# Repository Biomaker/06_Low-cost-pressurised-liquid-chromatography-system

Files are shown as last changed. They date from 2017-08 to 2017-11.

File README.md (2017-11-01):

## Open-source pressurised liquid chromatography system for the purification of proteins and small molecules

## Synopsis

Column chromatography is a routine technique for the separation of components from complex mixtures. In biochemistry and molecular biology, the most common application is the purification of recombinantly expressed proteins from in vitro or in vivo expression systems. These separations are currently performed by gravity flow, centrifugation or by using automated systems that use pumps to force solutions over a column. 

Gravity flow and centrifugation techniques, while simple and relatively inexpensive, are labour intensive and time consuming. Conversely, commercial systems allow a high degree of automation, limiting hands-on time, and allow more complex elution protocols, such as elution using salt or pH gradients. However, these systems require specialised, expensive equipment. The project proposed here aims to produce a lower cost, modular, open-source alternative to these commercial systems for performing simple, routine purifications.

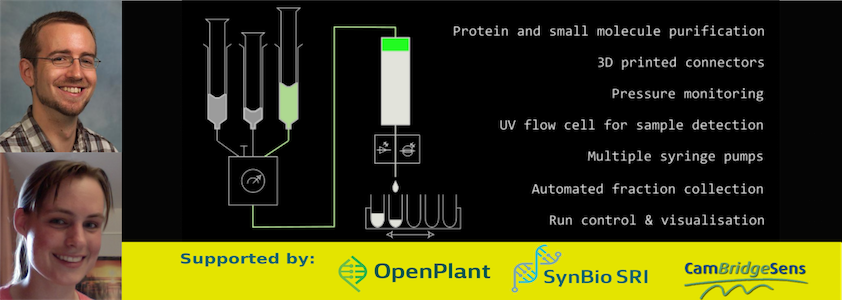
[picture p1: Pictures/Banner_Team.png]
Banner_image


## Overview Diagram

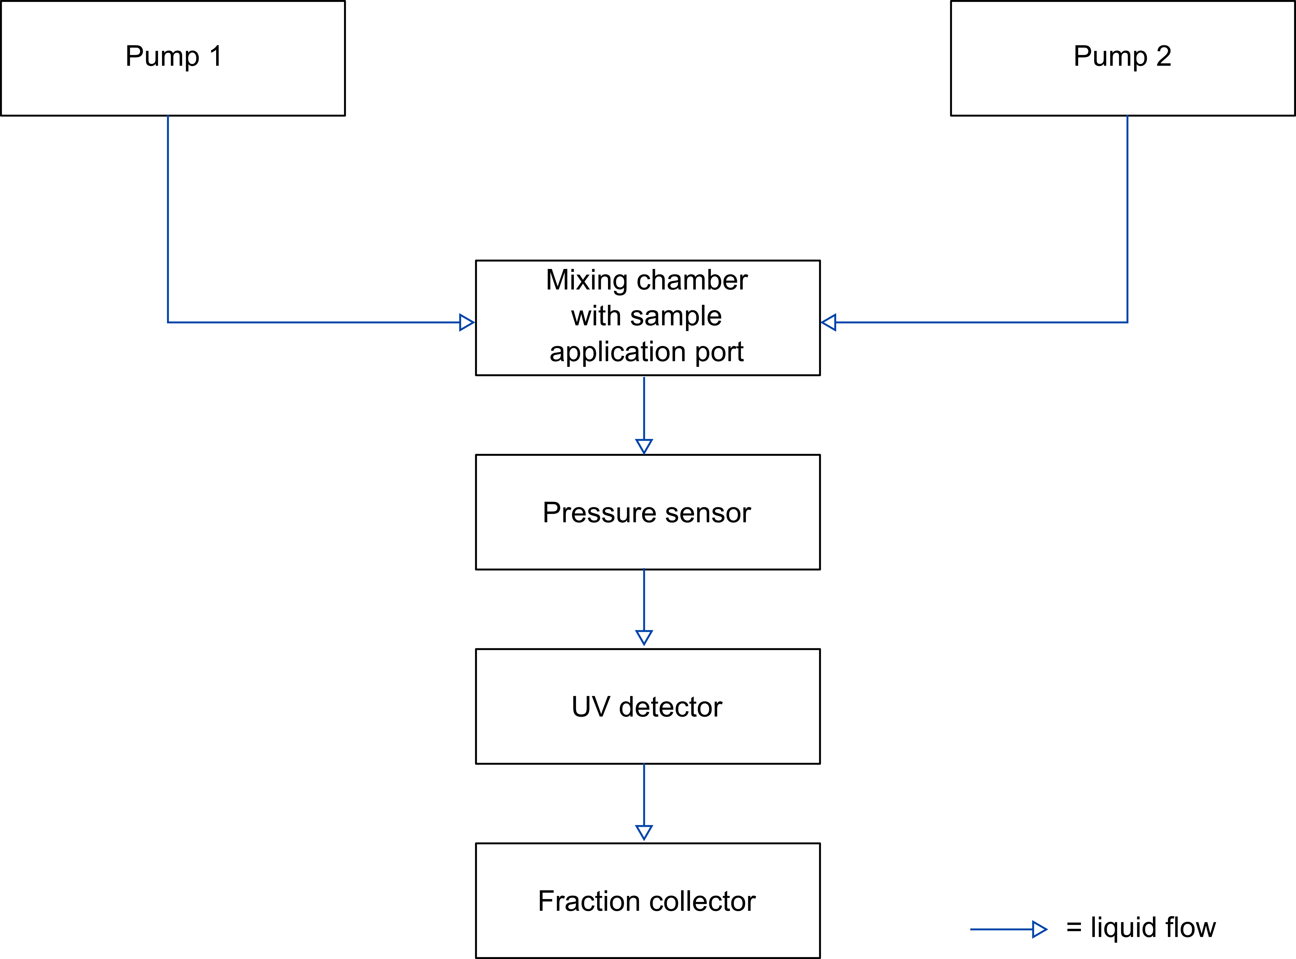
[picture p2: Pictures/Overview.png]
Project_overview


Diagram showing a high-level overview of the system. A typical method run for purification of a protein (preprogrammed in method runs) is as follows:
1) Connection of a chromatography column appropriate for the purification between the pressure sensor and UV sensor
2) Equilibration (conditioning) of the column using equilbration/wash buffer from pump 1
3) Loading of the sample through the sample application port on the mixing chamber
4) Washing of unbound material using equilbration/wash buffer from pump 1
5) Elution of the protein of interest from the column using elution buffer from pump 2
6) Steps 4 and 5 are accompanied by fractionation (separation of components) into different wells of a 96-well plate using the fraction collector

This project is a work in progress. For each component, navigate to the component folder for a list of known bugs and planned future improvements.

## Software
The project contains four Arduinos, one in each of two pumps, one in the fraction collector (SCARA arm) and one in the control unit. The control unit coordinates the other Arduinos and also reads out pressure sensor and UV sensor data. The SCARA arm Arduino controls the movements of the arm on prompting from the control unit over I2C. Pump Arduinos control the movement of the pumps after prompting by the control unit over I2C. For details of the software for each component, see the individual component folders.

## Hardware

The project contains different hardware modules, which are coordinated by the control module. For CAD files and diagrams, see individual component folders.

## Installation, Maintenance and Testing Guide

See individual component folders.

## Licenses

Hardware is distributed under the Creative Commons share alike license (see Thingiverse links). 
All software is available under the GNU General Public License Version 3 (https://www.gnu.org/licenses/gpl.html).

This project makes use of the following non-standard Arduino libraries, which are distributed under the indicated licenses:
1) Grove_LCD_RGB_backlight library - The MIT License (MIT) - Copyright (c) 2013 Seeed Technology Inc
2) MS5803-14 Master library for MS5803 14bar pressure sensor module - by Luke Miller (http://github.com/millerlp) -GNU General Public License Version 3

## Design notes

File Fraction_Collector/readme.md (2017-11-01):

 ## Fraction collector/SCARA Arm
 
 ## What does it do?
 A range of methods in a molecular biology laboratory is based splitting a sample in several sub-samples, commonly referred to as fractions. Depending on the method, fractions sometimes represent a spatial separation (e.g. when transferring liquids of ‘slices’ of a centrifugation tube into separate fractions), or temporal (e.g. when fraction are created from liquids running over a chromatography column). The common factor is that a certain amount of liquid is dispensed into a reservoir, then another one, then another one, and so on. Each of these fractions can then be treated independently  - to measure concentrations of compounds, enzymatic activities or just check what they smell like.
 
A fraction collector is fundamentally a piece of equipment that can hold a number of containers, and moves them about when required. 
 
 ## How is it implemented?
 
 Basic requirements:
-	use a flexible robotic arm with a small foot print when not in use
-	exchangeable tool head to accommodate a range of reservoirs

    o	SBS 96-well plate (shallow/deep)
    
    o	Eppendorf tubes
    
    o	Other reservoirs
    
-	Use common hardware from the 3D printing community
-	Focus on 3D printed parts to minimize commercial parts
-	Make something more exciting than a standard 2-axis plotter

We decided to use a 2D SCARA design (Selective Compliance Articulated Robot Arm) that was designed from scratch with an eye on minimizing exotic hardware. It is powered by NEMA 17 servos and Arduino hardware, using driver boards from the RepRap 3D printing community and cheap GT2 belts with 3D printed belt clamps. In order to save cost, we avoided optical or other encoders, and solely rely on an initial calibration step using microswitches to determine the absolute position of the arm. 

A carrier plate at the ‘wrist’ of the arm can hold a number of reservoirs, with the primary design focusing on standardized 96 well plates in an SBS format.  Other holders can be easily designed and programmed for.

The open source design should allow easy integration and adoption of this fraction collector for purposes other than chromatography
 
 ## Description of files
 Will be added when finished.
 
 ## Future work/Known bugs
 Future work:
 - add support for Eppendorff tubes and other reservoirs, other than the 96-well plate added so far
 
 Known bugs:
 - fraction collection is not accurate due to the code not taking into account the angle of the arm when aiming for the wells. Work is in progress on fixing the code

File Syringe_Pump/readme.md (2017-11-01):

## Syringe pumps

## What does it do?
A liquid chromatography setup relies on the controlled flow of liquid over a chromatography column. To provide this flow, we implement two syringe pumps, which can be programmed to flow at a desired flow rate. The system has two pumps, connected via a mixing chamber to potentially allow the use of a mixture of two buffers at ratios defined by the respective flow rates.

## How is it implemented?

## Description of files
Syringe_Pump_3_0_pump1 and Syringe_Pump_3_0_pump2 -> Arduino sketches, each controlling one pump. The only difference between the two sketches is the I2C address, which allows the pumps to be controlled from the control unit.

3D printer files -> contains CAD and 3D printer files for the syringe pump hardware

## Future work/Known bugs

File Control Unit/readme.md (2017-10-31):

## Control unit

## What does it do?
The control unit coordinates the function of the other components of the FPLC. It checks if all devices are connected and provides feedback. It then sends a signal to the fraction collector to start its calibration. Users can then choose from a number of options to run the FPLC system either manually, or make use of pre-programmed methods.

To save on Arduinos and reduce communication, the control unit also reads out the values from the pressure and UV sensors in our implementation. 

## How is it implemented?
The control unit communicates with the other devices over I2C. For display, it uses the Seeed kit Grove RGB LCD. To navigate the menus, it makes use of five buttons, connected via different resistors to one analog pin on the Arduino. Depending on the analog value received, the Arduino can determine which button has been pressed.

The menu layout is as follows:
1) Start/Welcome screen
2) Check I2C communication to all connected devices and display if devices are connected - allow user to repeat the test if desired
3) Start fraction collector calibration
4) Allow choice between Manual Run or Method Run:

5) Manual Run - Select either which pump to run at which speed -> this will trigger the selected pump and tell it to run at the speed specified via I2C, or select Display sensor values. Display sensor values will display current values from the pressure sensor (in bar) and the UV sensor

6) Method Run - Currently the unit has two pre-programmed methods- a pump wash method, which will first run pump 2 and then pump 1 to wash out residual buffer from a previous run and prefill the tubing with the solution from pump 1. The second method is a standard run method, which first runs pump 1, pauses to allow loading of the sample, runs pump 1 while collecting fractions and then runs pump 2 while collecting fractions. During the entire program, UV and pressure sensor readings are displayed. The current program assumes a 1 ml column.

For implementation of the UV sensor and pressure sensor, see the respective subfolders.

## Description of files
Control_unit_1_4                      -> latest Arduino sketch for running the control unit

MCU v3.step                           -> CAD file for control unit enclosure

MCU_base.stl and MCU_cover.stl        -> 3D printer files for enclosure

Fritzing Files                        -> Diagrams for the pressure sensor and a Fritzing file for the circuit

MCU_BOM_electronics.md                -> Bill of materials for the electronics

MCU_Fritzing.pdf                      -> Picture of the Fritzing breadboard diagram buttons are (from left to right) - UP, DOWN, LEFT, RIGHT, SELECT

## Future work/Known bugs/issues

Future work:
- Bug fixing - see below
- Allow saving of the UV and pressure sensor information to an SD card
- Allow display of the UV and pressure sensor information as it relates to the fractions after the run
- Build a display and analysis program on a Raspberry Pi for display and processing of run data
- Allow user to add pre-programmed methods using the display and analysis program

Known bugs:
- UV sensor readings are not very sensitive and too low to be of use - could potentially be fixed by reducing the flow path distance and using a more powerful UV light source

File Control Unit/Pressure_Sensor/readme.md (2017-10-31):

## Pressure Sensor

## What does it do?
In a liquid chromatography system, the column represents a key component. Resins with specific properties tend to be expensive, and can be easily damaged by incorrect handling. 

The rate at which samples or liquids can be pushed through the column is not constant, and can be drastically reduced if a column is overloaded. If the flow rate is not reduced at this point, the column or other components can be damaged by the increasing back pressure.

## How is it implemented?
We decided to use the  MS5803-14BA sensor, as it can communicate by I2C and is protected against the liquid phase by a gel membrane cover. 

We bought a non-integrated sensor to minimize cost, but would advise against this course of action, as the SMD packaging format makes soldering difficult. We succeeded in soldering the sensor to an SMT breakoutPCB for SOIC-8 from Adafruit (Product nr. 1212), using a hot plate and a heat gun. For easier use, we would recommend the SparkFun Pressure Sensor Breakout Board MS5803-14BA (SEN-12909).

The sensor is integrated into the chromatography setup using a 3D printed part with a suitable cut-out for the sensor. The sensor and board were constrained by a clamp, and any gaps closed by silicone sealant. 

To allow reading of the sensor values using an Arduino, we made use of the MS5803-14 Master library by Luke Miller, which can be found at http://github.com/millerlp. His repository also contains sketches for testing the sensor, which we used to verify our sensor was working prior to integration into the control unit.

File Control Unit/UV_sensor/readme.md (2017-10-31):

## UV flow cell

## What does it do?
During a chromatography run the protein of interest is held back on the column until a specific buffer reaches the column and washes the protein off the column – this is referred to as elution. The fraction collector will create a sequential series of samples coming off the column, some of which will contain the protein.  How can we identify which fractions are valuable to us?

Most proteins in solution can not be seen by the naked eye in the visible light spectrum, but a majority absorbs UV light. By shining a constant amount of UV light through the sample and measuring how much UV light exits at the other side of the sample, we can identify fractions that contain the largest amount of protein and therefore absorb the largest amount of UV light This can either be done after the purification is finished, but most modern FPLC systems would constantly monitor these measurements while the sample is separated into fractions.

Proteins that contain amino acids with aromatic rings (Tryptophan, Tyrosine) absorb light at 280 nm (UV). In a photometer, light is filtered down to a specific wavelength or wavelength range, directed through the sample and the transmitted light detected. The resulting signal is dependent on the distance through the sample, the concentration of protein in the sample and the specific absorption coefficient. This relationship is described by the Beer-Lambert Law.

## How is it implemented?

Requirements:
-	small volume in the flow cell to minimize dead volume 
-	280 nm light must not be absorbed by the container
-	pressure proof
-	280 nm light must be contained to ensure safety
-	cheap

Commercial flow cells tend to cost hundreds of pounds. They rely on glass or quartz chambers which are UV permissive, and use strong, wide-band light sources to allow flexible measurements of various wavelengths, to allow flexible detection of various compounds depending on the application. 

We decided to create a cheap flow cell based on disposable plastic cuvettes that are transparent to UV light. They create a 10 mm path length through the sample, but are normally not suited to continuous usage. By designing a custom 3D printed plug, we created a small enclosed chamber around the light path, with two tubes allowing continuous flow into and out of the cuvette. 
Monochromators, which filter out unwanted wavelengths, are similarly complex and expensive. We therefore bought a 12V 280nm UV LED, with a  narrow emission spectrum, and combined it with a cheap wideband UV detector (280-390nm). While this would normally be not desirable, in a closed system the vast majority of the signal will be generated by the 280nm LED.

The 3D printed enclose creates a housing for the plastic cuvette, creates holders for both the LED and the UV detector and allows a tight connection with the plug. Generous use of silicone sealant both avoids leakage of liquids and light outside the desired light path.

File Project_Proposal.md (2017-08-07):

## Summary
Column chromatography is a routine technique for the separation of components from complex mixtures. In biochemistry and molecular biology, the most common application is the purification of recombinantly expressed proteins from in vitro or in vivo expression systems. These separations are currently performed by gravity flow, centrifugation or by using automated systems that use pumps to force solutions over a column. 
Gravity flow and centrifugation techniques, while simple and relatively inexpensive, are labour intensive and time consuming. Conversely, commercial systems allow a high degree of automation, limiting hands-on time, and allow more complex elution protocols, such as elution using salt or pH gradients. However, these systems require specialised, expensive equipment. The project proposed here aims to produce a lower cost, modular, open-source alternative to these commercial systems for performing simple, routine purifications.

## Proposal
Systems to be used and problems to be addressed
Research into protein structure and function relies heavily on the availability of highly pure proteins. These are routinely produced in recombinant expression systems and purified using a variety of chromatography methods, such as affinity purification, ion exchange or size exclusion chromatography.
 
There are a variety of methods available for applying samples and solutions to chromatography columns, each with their advantages and disadvantages. Gravity flow and spin column purification, while having the advantage of being relatively low-cost, are labour intensive, requiring manual sample and buffer addition and are also limited in terms of complexity of the elution conditions. Gravity flow and spin column purification are therefore mainly used for the purification of limited amounts of protein using various types of affinity purification. For large-scale purifications or purification requiring more complex elution conditions, such as salt or pH gradients, automated FPLC (fast protein liquid chromatography) systems are commonly used. These systems use pumps to force solutions over chromatography columns at pressure and thereby reduce run time. They also allow the use of preprogrammed complex purifications to take place without manual intervention. Their major drawback is their cost, with entry level models starting at roughly 5,000 GBP.
 
## Design goals and implementation 
We aim to create a system that sits in between the manual purification methods and the fully automated, specialised systems. The goals and proposed design steps for this system are as follows:

1)	Automate a gravity flow procedure with automated sample loading, washing and elution using a single elution buffer (step elution) for affinity purification. 
Initially, we will use three syringe pumps for wash solution, elution solution and sample solution respectively. These will be placed on a 3D-printed rack, to allow them to be moved with respect to the column. For the syringe-based pump system, we will adapt an existing open-source design, described here: (http://www.appropedia.org/Open-source_syringe_pump). We aim to allow for programming of the device via a simple UI on an embedded screen.

2)	Automated fraction collection
The fraction collector will take the form of a movable tube rack. The design will be based on a linear slider mechanism that will be either 3D printed or based on aluminium extrusions.

3)	Conversion of the gravity flow system to a pressurised closed system
We intend to use standard connectors (e.g. Luer) and silicone or Tygon tubing to connect the syringe pumps to the chromatography column. We will attempt to 3D print suitable connectors to maximize the usage of non-commercial parts. 

4)	On-line detection of protein using a custom-built detection module, display of results on fraction rack
To allow monitoring of the purification, we will add a detection module to the column outlet. This detection module will monitor protein concentration by absorbance at 280 nm in solution using a suitable UV LED and photodetector. Absorbance over time will be displayed on the embedded screen as well as on embedded LEDs in the fraction rack to indicate directly which tubes contain eluted protein.

More ambitious, additional goals, depending on success of initial designs would include:

1) Addition of valves/mixing chambers to the pump system to allow buffer mixing for running gradient elutions

2) Design of additional detection modules (e.g. DNA, absorbance at 260 nm) or fluorescence detection, which can be added to, or replace the 280 nm detector.

3) Addition of multiple pump and detector modules to allow parallel purification of multiple samples.

## Proposed outcomes and benefits
The major outcome of this project would be a low-cost, automated protein purification system, which could be used for simple, routine purifications in settings where gravity flow is too time consuming, but the cost of a commercial system is prohibitive. The open-source design will allow users to easily replace damaged parts as well as add to and customise the modules. Given the expected cost, we also see a use as a teaching tool for schools, undergraduate labs and biomaker spaces, to teach more advanced protein purification techniques and introduce students to the concept of automation in protein purification. The final 3D models, parts list, circuit diagrams, code and guides on replicating the project will be made available on Github for easy replication of the project.

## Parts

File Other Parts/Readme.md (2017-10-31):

This folder contains the 3D files for non-major devices. Including:
- the housing for the pressure sensor (required 2 knurled brass insert nuts & solid amount of glue)
- the swing arm to hold the tubing over the fraction collector (with mounting point for a laser module)
- the mixing unit to combine liquid from two pumps (requires more knurled brass insert nuts and two 3-way luer loc valves)

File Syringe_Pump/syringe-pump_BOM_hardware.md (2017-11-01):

Syringe Pump

Bill of materials 

-	Core 3D printed parts
-	1 x Stepper Motor NEMA-17 Size - 200 Steps/Rev, 12V 350mA
-	ProtoShield Protoyping Board for Arduino
-	1 x StepStick 4-layer DRV8825 Stepper Motor Driver boards
-	12V DC Connector 2.1x5.5mm DC Power Cable Jack Adapter
-	
-	3 x button microswitch
-	1 x 5 mm LED
-	2 x 30 cm 6mm steel rod 30 cm (depending on syringe)
-	1 x 30 cm M5 threaded rod 30 cm
-	1 x shaft coupler M5 
-	2 x LM6UU linear bearing 6 mm
-	1 x M5 knurled thumb nut, thin type (or other flat, wide M5 nut)
-	Various M3 screws for assembly 

Notes:

Top plate: print with 10-20% infill to create a sturdy structure. The linear bearings should fit snugly into the slots, 
same with the thumb screw (perhaps fix all with a dab of glue once the threaded rod holds it in place). 
The current version is designed for most 50/60ml syringes, but we have encountered syringes with unusual 
thickness/shape at the top of the plunger that wouldn’t fit – carving for a few minutes with a Stanley 
knive (on the syringe, not the 3D printed part) usually solved any problems.

Syringe adapter: The luer loc doesn’t fit perfectly yet, and will probably leak. 
Install a brass nut insert at the bottom (use a mixture of heat (soldering iron) and epoxy to fuse it tightly into the PLA), 
and then install the tubing with the printed connector screw, a rubber o-ring and any other sealing helpers (silicone, Teflon tape).  
Verify water tight fit, then install in the base unit. 

Base assembly: This is somewhat tight. A standard Arduino Uno just about fits into the base, and will support some of the pressure from the top. 
The vertical rods are supposed to be connected to two wires to carry power to the emergency off (maximum) button switch 
sitting on the holder. Conductive ink helps connector the wires in the 6mm rod slots to the rods themselves, otherwise soldering is an option. 
Similarly, the horizontal clamp has a slot for a short wire & a button switch to allow the pump to sense when it shouldn’t move any lower.
Install the two button switches & the LED at the front of the base.
Mount the Arduino against the vertical wall with two screws.
Fix the 12V connector in place with the clamp (and/or some glue). 
Place the finished prototyping board on top, then carefully close up the base. 

If it doesn't click into place, check for wires that got in the way.

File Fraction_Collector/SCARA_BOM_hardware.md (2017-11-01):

SCARA fraction collector

Bill of materials 

-	Core 3D printed parts: upper & lower arm, base, top 
-	Extra 3D printed parts: plate holder, switch housing, Arduino housing
-	https://www.thingiverse.com/thing:2613742
-	2 x Stepper Motor NEMA-17 Size - 200 Steps/Rev, 12V 350mA
-	2 x 2GT / GT2 timing belt sprocket, 20 teeth
-	1 meter 2GT / GT2 belt
-	3 x belt clamps (3D printed, https://www.thingiverse.com/thing:2503261)
-	Arduino Mega
-	ProtoShield Protoyping Board for Arduino
-	2 x StepStick 4-layer DRV8825 Stepper Motor Driver boards
-	4 x SPDT NO+NC KW12 Straight Hinge Lever Control Mini Micro Switch
-	6 x 625z ball bearings
-	12V DC Connector 2.1x5.5mm DC Power Cable Jack Adapter
-	M5 screws (e.g. M5 30-40mm connector bolt)
-	6 mm smooth steel rod, 10-30cm
-	2 x M5 binding screw 33mm (or normal M5 & nuts, for the elbow)
-	10 x M3 screws (3-5mm)
-	Silly amounts of wire
-	Some glue
-	Extra electronics (resistors, etc) see wiring diagrams. 

Notes: 
2GT / GT2 profiles for the arms are designed according to the official specification, 
with the sprocket on either arm sporting 90 teeth, matched to a 20 teeth sprocket on the stepper motor. 

Print parts and remove support structures as required.
Add 625z ball bearings into both arms and the roller unit, perhaps fix with a dab of glue (depending on the print quality).
Cut 2GT /GT2 belt to size, assemble around the arm and fix with the belt clamps. 
Adjust tension carefully – preferably when the arm is mounted to the base.
Adjust the relative positions of the belt clamps if they block each other during operations.
Glue microswitches into the housing (recommend rear-most slot on the side, lever facing up & lever facing down at the front).

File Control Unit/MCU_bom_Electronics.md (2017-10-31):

<!DOCTYPE html PUBLIC "-//W3C//DTD XHTML 1.0 Transitional//EN" "http://www.w3.org/TR/xhtml1/DTD/xhtml1-transitional.dtd">
<html xmlns="http://www.w3.org/1999/xhtml">
<body>
<h1>Bill of Materials: MCU.fzz</h1>
<p class="meta">MCU.fzz</p>
<p class="meta">Tuesday, October 31 2017, 23:30:00</p>

<h2>Assembly List</h2>
<table>

  <thead>
   <tr>
    <th>Label</th>
    <th>Part Type</th>
    <th>Properties</th>
    </tr>
  </thead>
  <tbody>
  <tr>
    <td>C1</td>
    <td>Ceramic Capacitor</td>
    <td class="props">voltage 6.3V; package 200 mil [THT, multilayer]; capacitance 100nF</td>
</tr><tr>
    <td>Grove1</td>
    <td>Grove RGB LCD 2 x 16</td>
    <td class="props">size 2 x 16; interface I2C; variant variant 13</td>
</tr><tr>
    <td>MS5803-14BA1</td>
    <td>MS5803-14BA Pressure Sensor</td>
    <td class="props">variant variant 1</td>
</tr><tr>
    <td>Part1</td>
    <td>Arduino Uno (Rev3) - ICSP</td>
    <td class="props">type Arduino UNO (Rev3) - ICSP (w/o icsp2)</td>
</tr><tr>
    <td>Part2</td>
    <td>Logic Level Converter</td>
    <td class="props"></td>
</tr><tr>
    <td>Part3</td>
    <td>GUVA-S12SD UV Light Sensor</td>
    <td class="props">variant variant 1</td>
</tr><tr>
    <td>R1</td>
    <td>220Ω Resistor</td>
    <td class="props">resistance 220Ω; package 0603 [SMD]; tolerance ±5%</td>
</tr><tr>
    <td>R2</td>
    <td>560Ω Resistor</td>
    <td class="props">resistance 560Ω; package 2512 [SMD]; tolerance ±5%</td>
</tr><tr>
    <td>R3</td>
    <td>1.7kΩ Resistor</td>
    <td class="props">resistance 1.7kΩ; package 2512 [SMD]; tolerance ±5%</td>
</tr><tr>
    <td>R4</td>
    <td>4.7kΩ Resistor</td>
    <td class="props">resistance 4.7kΩ; package 2512 [SMD]; tolerance ±5%</td>
</tr><tr>
    <td>R5</td>
    <td>10kΩ Resistor</td>
    <td class="props">resistance 10kΩ; package 2512 [SMD]; tolerance ±5%</td>
</tr><tr>
    <td>R6</td>
    <td>10kΩ Resistor</td>
    <td class="props">resistance 10kΩ; package 2512 [SMD]; tolerance ±5%</td>
</tr><tr>
    <td>R7</td>
    <td>10kΩ Resistor</td>
    <td class="props">resistance 10kΩ; package 0603 [SMD]; tolerance ±5%</td>
</tr><tr>
    <td>R8</td>
    <td>10kΩ Resistor</td>
    <td class="props">resistance 10kΩ; package 0603 [SMD]; tolerance ±5%</td>
</tr><tr>
    <td>S1</td>
    <td>Pushbutton</td>
    <td class="props">package [THT]</td>
</tr><tr>
    <td>S2</td>
    <td>Pushbutton</td>
    <td class="props">package [THT]</td>
</tr><tr>
    <td>S3</td>
    <td>Pushbutton</td>
    <td class="props">package [THT]</td>
</tr><tr>
    <td>S4</td>
    <td>Pushbutton</td>
    <td class="props">package [THT]</td>
</tr><tr>
    <td>S5</td>
    <td>Pushbutton</td>
    <td class="props">package [THT]</td>
</tr>
  </tbody>
</table>
<h2>Shopping List</h2>
<table>
  <thead>
	<tr>
    <th>Amount</th>
    <th>Part Type</th>
    <th>Properties</th>
    </tr>
  </thead>
  <tbody>
<tr>
    <td>1</td>
    <td>Ceramic Capacitor</td>
    <td class="props">voltage 6.3V; package 200 mil [THT, multilayer]; capacitance 100nF</td>
</tr><tr>
    <td>1</td>
    <td>Grove RGB LCD 2 x 16</td>
    <td class="props">size 2 x 16; interface I2C; variant variant 13</td>
</tr><tr>
    <td>1</td>
    <td>MS5803-14BA Pressure Sensor</td>
    <td class="props">variant variant 1</td>
</tr><tr>
    <td>1</td>
    <td>Arduino Uno (Rev3) - ICSP</td>
    <td class="props">type Arduino UNO (Rev3) - ICSP (w/o icsp2)</td>
</tr><tr>
    <td>1</td>
    <td>Logic Level Converter</td>
    <td class="props"></td>
</tr><tr>
    <td>1</td>
    <td>GUVA-S12SD UV Light Sensor</td>
    <td class="props">variant variant 1</td>
</tr><tr>
    <td>1</td>
    <td>220Ω Resistor</td>
    <td class="props">resistance 220Ω; package 0603 [SMD]; tolerance ±5%</td>
</tr><tr>
    <td>1</td>
    <td>560Ω Resistor</td>
    <td class="props">resistance 560Ω; package 2512 [SMD]; tolerance ±5%</td>
</tr><tr>
    <td>1</td>
    <td>1.7kΩ Resistor</td>
    <td class="props">resistance 1.7kΩ; package 2512 [SMD]; tolerance ±5%</td>
</tr><tr>
    <td>1</td>
    <td>4.7kΩ Resistor</td>
    <td class="props">resistance 4.7kΩ; package 2512 [SMD]; tolerance ±5%</td>
</tr><tr>
    <td>2</td>
    <td>10kΩ Resistor</td>
    <td class="props">resistance 10kΩ; package 2512 [SMD]; tolerance ±5%</td>
</tr><tr>
    <td>2</td>
    <td>10kΩ Resistor</td>
    <td class="props">resistance 10kΩ; package 0603 [SMD]; tolerance ±5%</td>
</tr><tr>
    <td>5</td>
    <td>Pushbutton</td>
    <td class="props">package [THT]</td>
</tr>
  </tbody>
</table>
<p class="meta"><br/>Exported with Fritzing 0.9.3- http://fritzing.org</p>
</body>
</html>

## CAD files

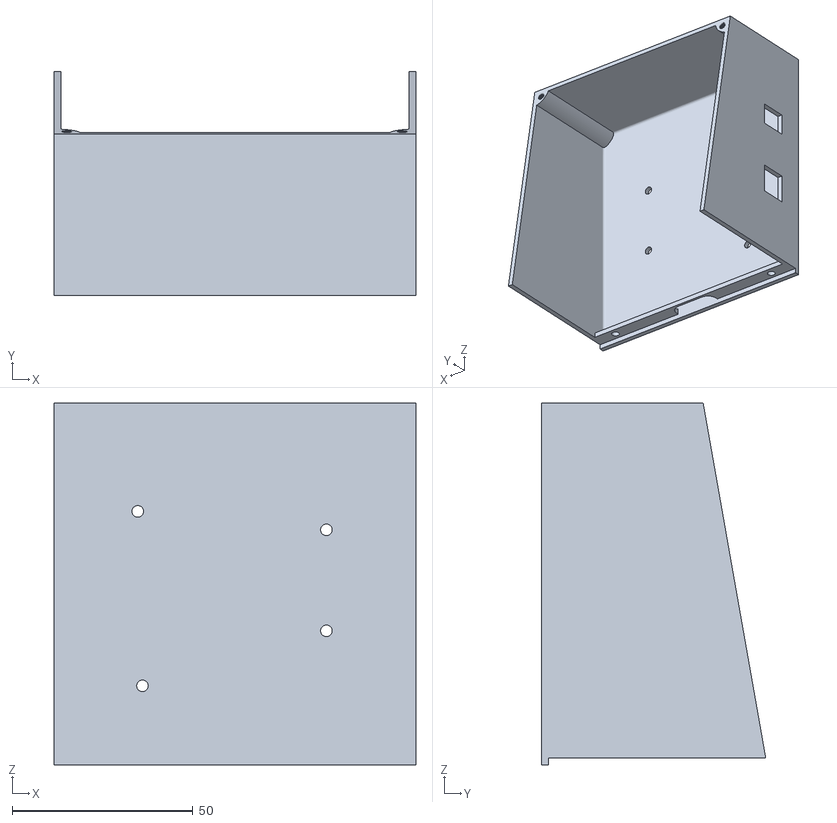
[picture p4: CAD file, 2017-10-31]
Control Unit/MCU_base.stl
100.0 x 62.0 x 100.0

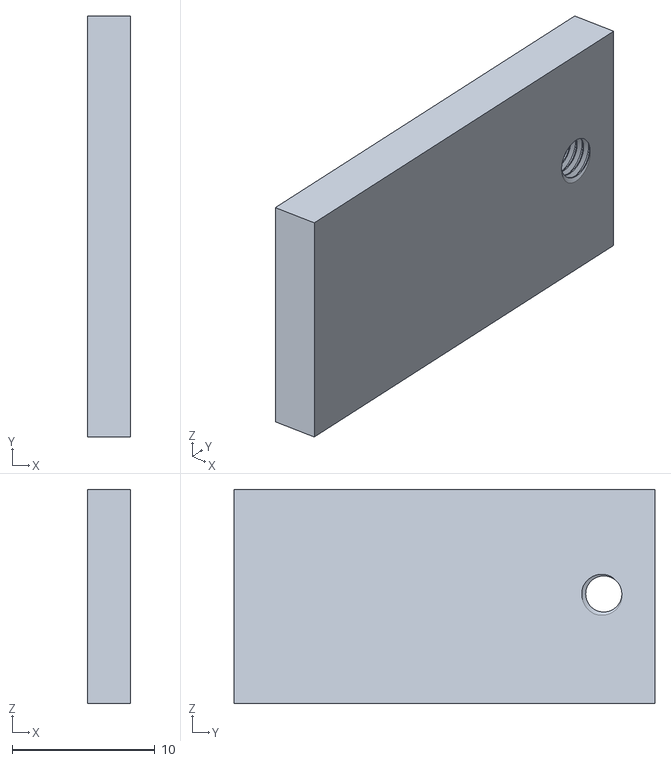
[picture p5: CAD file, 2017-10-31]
Control Unit/UV_sensor/flowcell_cover_led.stl
3.00 x 29.5 x 15.0

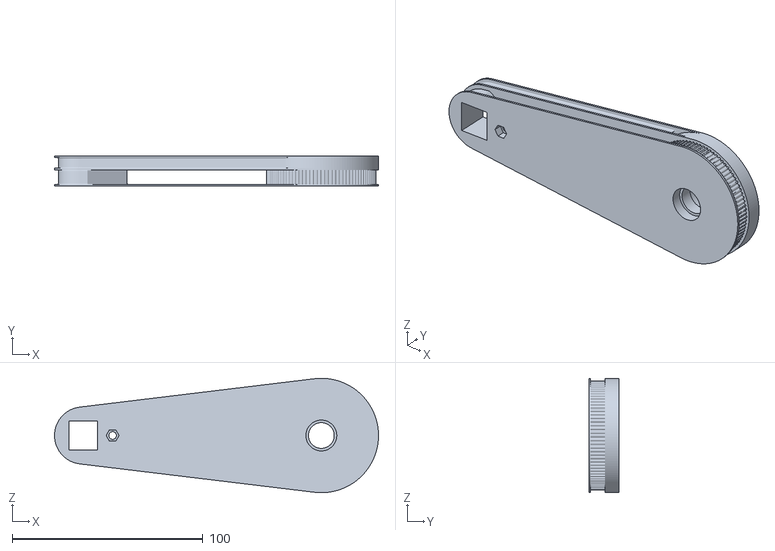
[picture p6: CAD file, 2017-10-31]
Fraction_Collector/3D printer files/scara_lowerarm.stl
170.0 x 16.0 x 60.0

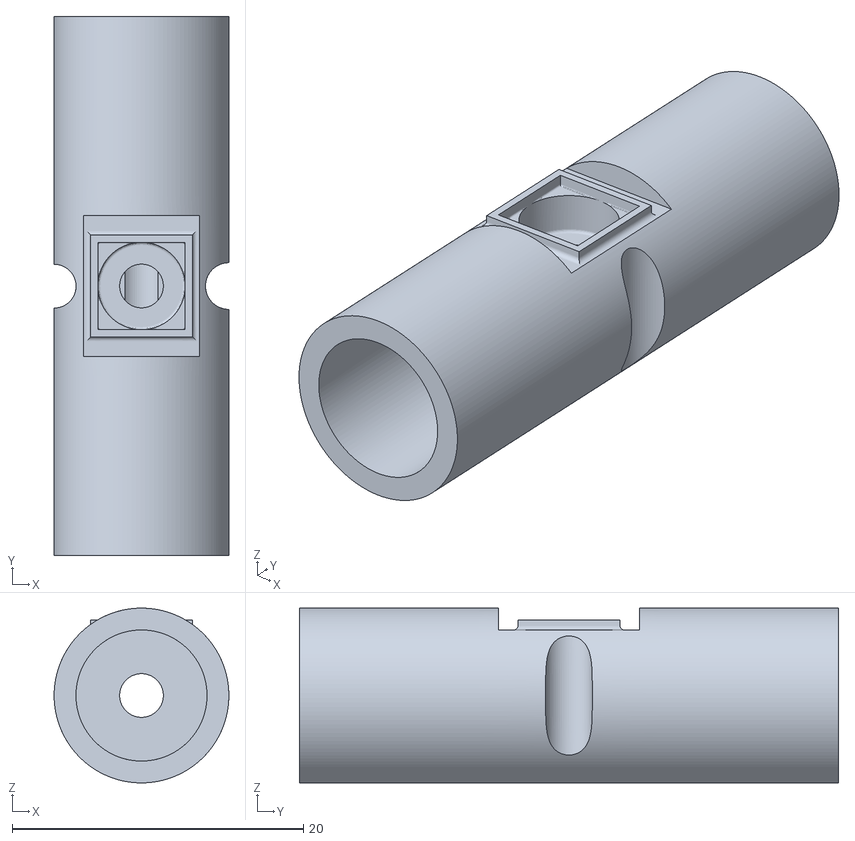
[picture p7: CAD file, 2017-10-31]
Other Parts/pressure_sensor_housing.stl
12.0 x 37.0 x 12.0

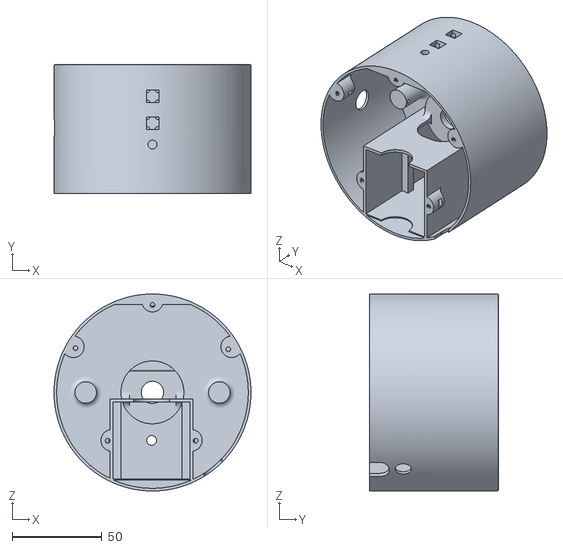
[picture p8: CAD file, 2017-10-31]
Syringe_Pump/3D printer files/pump_base.stl
110.0 x 72.0 x 110.0

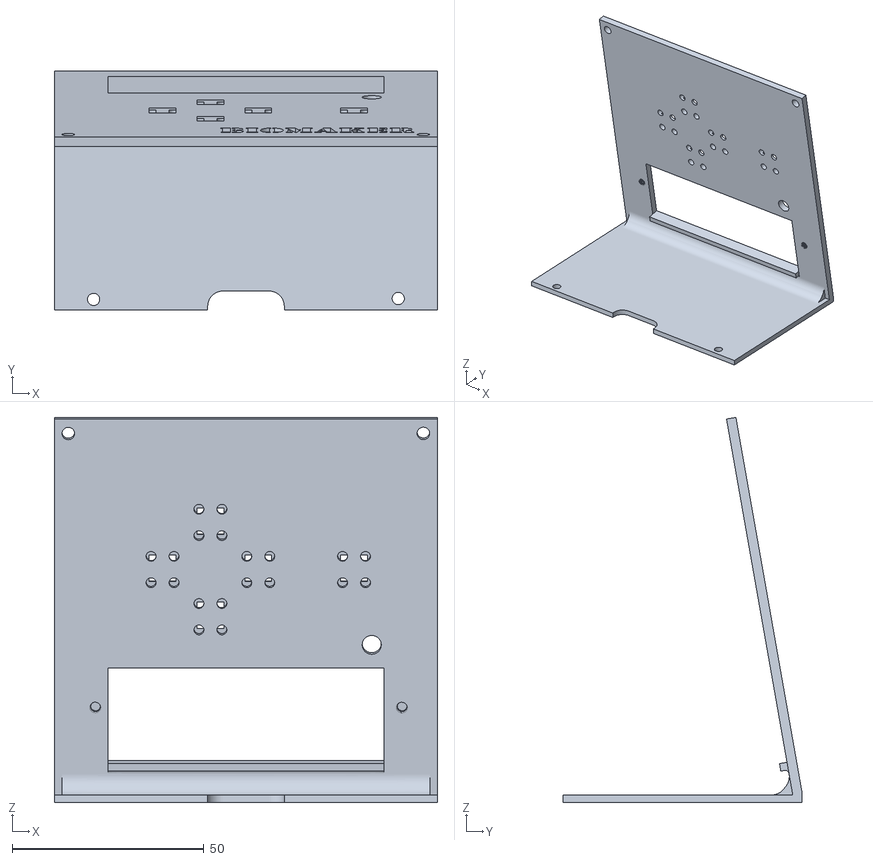
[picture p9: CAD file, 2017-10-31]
Control Unit/MCU_cover.stl
100.0 x 62.5 x 100.6

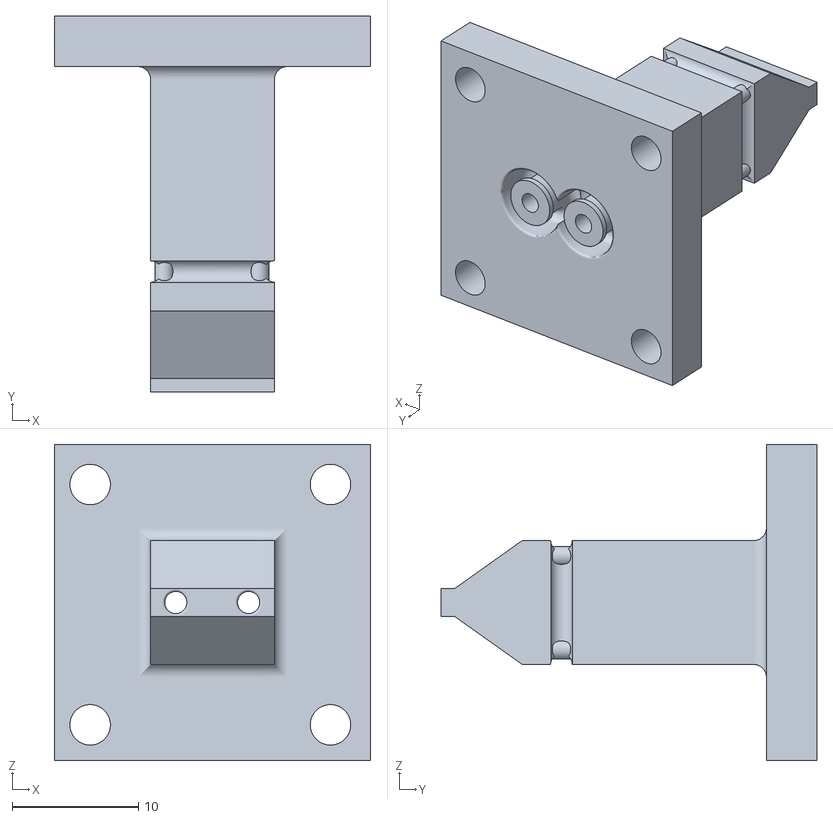
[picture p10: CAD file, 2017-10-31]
Control Unit/UV_sensor/flowcell_plug.stl
25.0 x 29.7 x 25.0

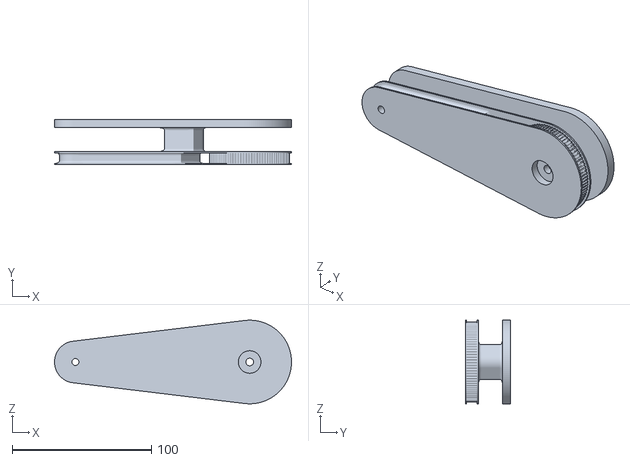
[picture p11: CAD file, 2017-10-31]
Fraction_Collector/3D printer files/scara_upperarm.stl
170.0 x 32.5 x 60.0

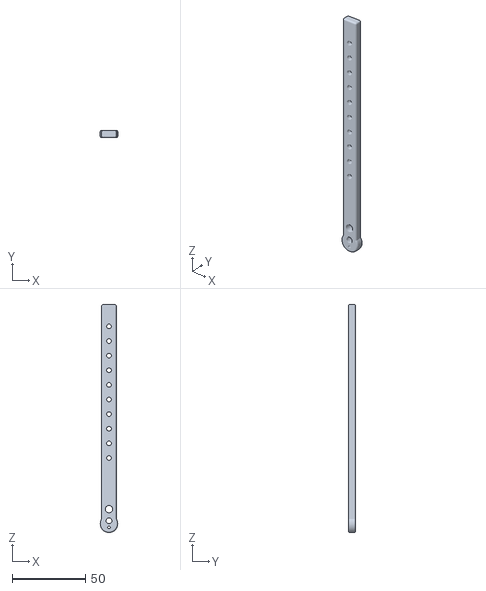
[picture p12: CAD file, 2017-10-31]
Other Parts/swingarm_inner.stl
12.0 x 5.00 x 156.0

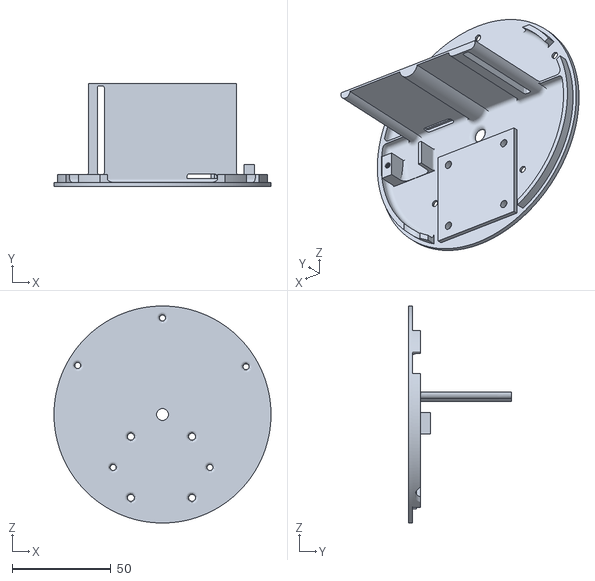
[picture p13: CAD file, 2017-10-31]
Syringe_Pump/3D printer files/pump_baseplate.stl
110.0 x 52.1 x 110.0

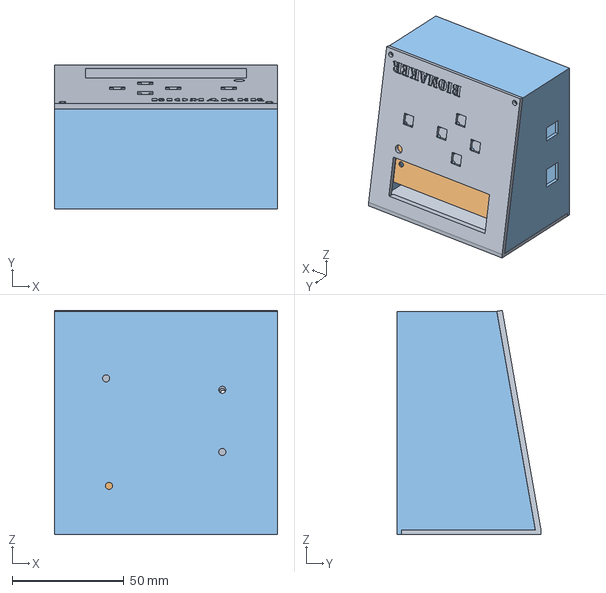
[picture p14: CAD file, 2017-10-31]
Control Unit/MCU v3.step
100.0 x 64.5 x 100.6 mm

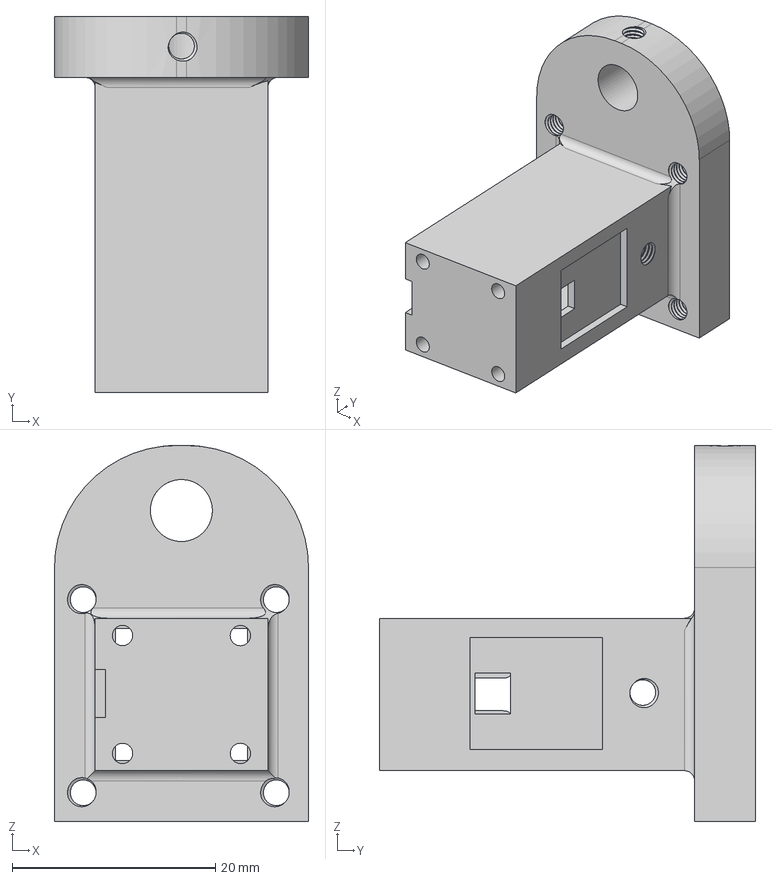
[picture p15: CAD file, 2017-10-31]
Control Unit/UV_sensor/UV flow cell_2tubes_uv components v14.step
25.0 x 37.0 x 37.0 mm

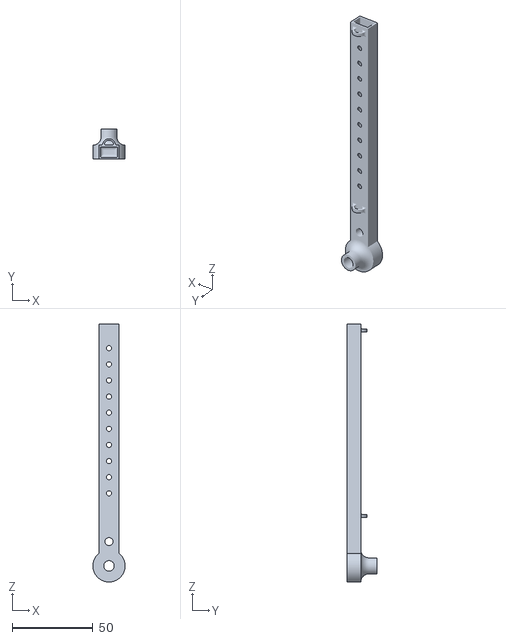
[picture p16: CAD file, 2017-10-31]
Other Parts/swingarm_outer.stl
20.0 x 18.5 x 160.0

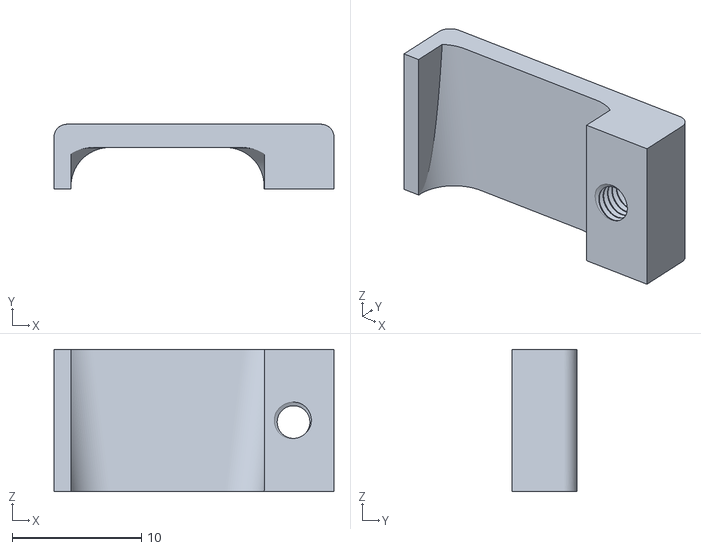
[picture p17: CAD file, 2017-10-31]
Syringe_Pump/3D printer files/pump_12Vclamp.stl
21.7 x 5.00 x 11.0

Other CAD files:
Fraction_Collector/3D printer files/scara_clean_housing v21.step
Control Unit/UV_sensor/flowcell_holder.stl
Fraction_Collector/3D printer files/scara_topholder.stl
Other Parts/mixer_unit.stl
Control Unit/UV_sensor/flowcell_cover_detector.stl
Fraction_Collector/3D printer files/SCARA_NEMAhousing.stl
Fraction_Collector/3D printer files/SCARA_SBSplateholder.stl
Fraction_Collector/3D printer files/SCARA_arduinomega_housing.stl
Fraction_Collector/3D printer files/SCARA_rearcover.stl
Fraction_Collector/3D printer files/scara_switch_housing.stl
Syringe_Pump/3D printer files/pump_adapterluer.stl
Syringe_Pump/3D printer files/pump_clamp.stl
Syringe_Pump/3D printer files/pump_top.stl
Syringe_Pump/3D printer files/screw_connector.stl

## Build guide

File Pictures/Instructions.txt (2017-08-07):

Deposit pictures associated with the project here (Banners, photos etc.)

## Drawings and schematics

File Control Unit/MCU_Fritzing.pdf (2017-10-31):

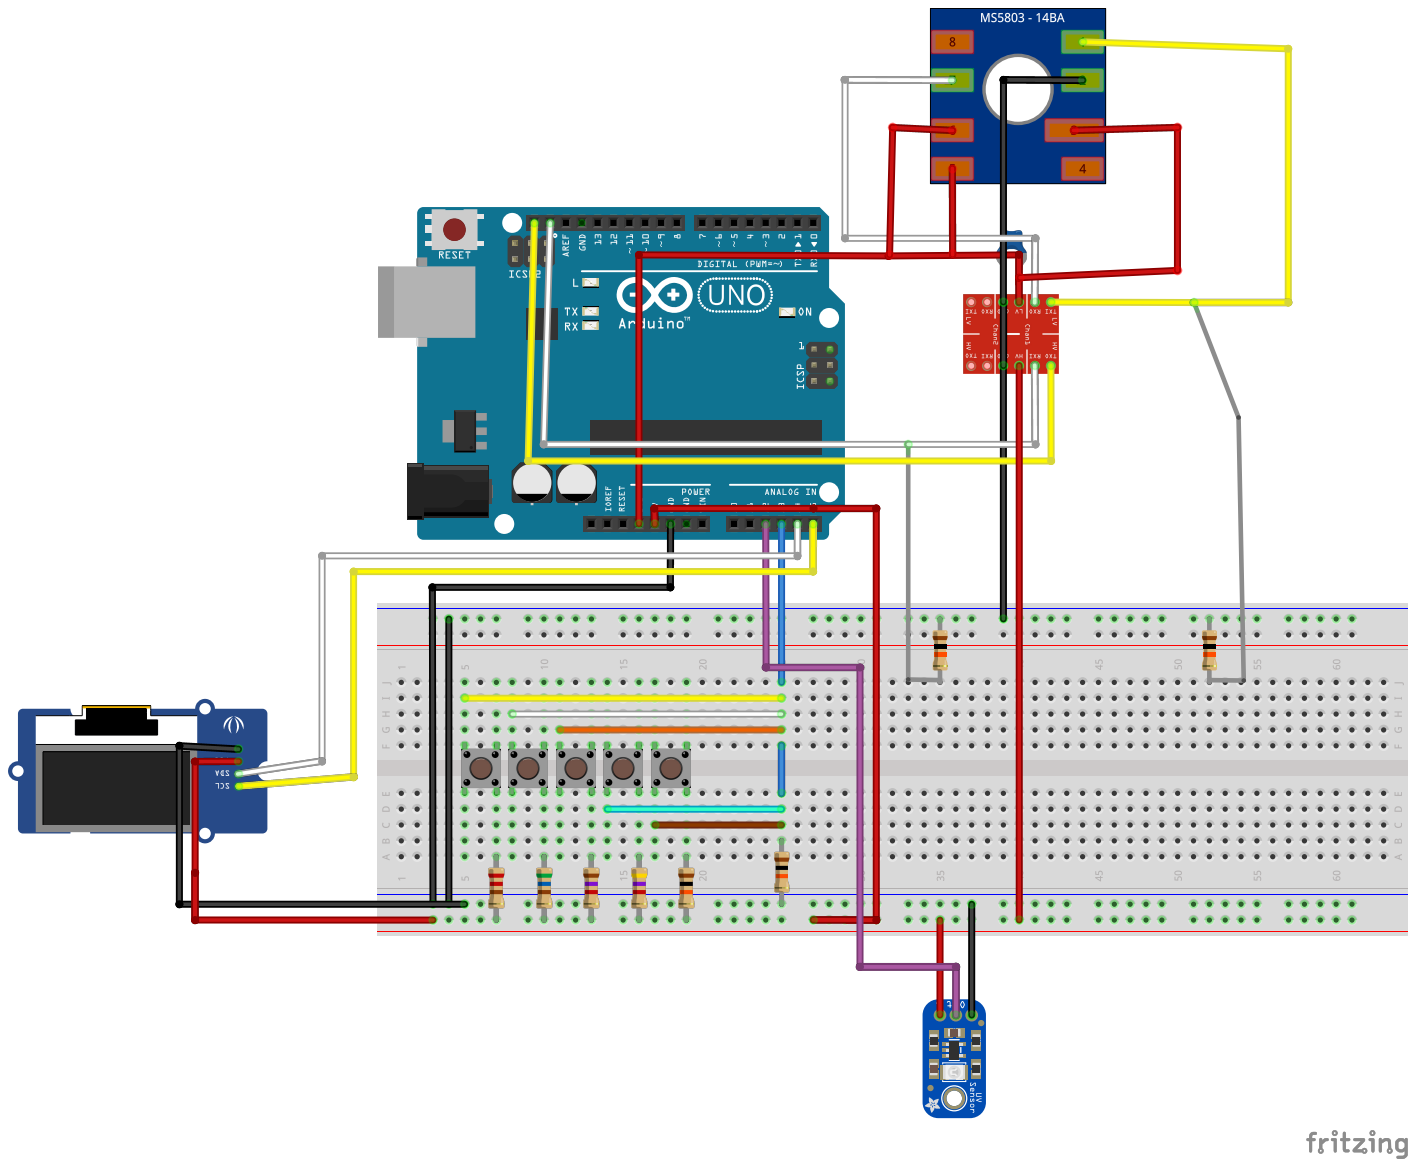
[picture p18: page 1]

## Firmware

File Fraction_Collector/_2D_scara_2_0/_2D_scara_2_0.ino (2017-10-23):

 /*Script that drives a 2D SCARA arm to a defined (X,Y) position. 
 *version 1.9 - allows fraction collection on demand by the control unit using pulses 
*Version 1.8 fixed bugs in calibration function,removed unneccessary comments and added more code commenting
*Version 1.6 - added calibration function - prompted by the control unit over I2C
*Version 1.5 - added microstepping capability (required for accuracy) - had to disable calibration - no more digital pins - writing code to do this via one analog pin atm
 * Version 1.4 - added calibration for the shoulder joint
 *Version 1.3 - added 96 well plate fractionation
 *Version 1.2 - fixed bugs and added button input support
 * UPDATE:
 * Can now use MoveUsingSerial(); to move the arm to different X and Y positions using the serial monitor. Can also use MoveUsingButtons(); to
 * drive the arm using 4 directional buttons. This setup uses the Gtronics protoyping board, so all buttons are wired to one analog input pin via
 * different resistors. The sketch decides based on the input voltage which button was pressed.
 * 
 * For using this sketch in other applications:
 * 1) Save the current position using SaveArmPosition()
 * 2) Set the target (x,y) point for the hand using SetTarget(X,Y)
 * 3) Calculate the position of the elbow joint using CalculateElbowPosition()
 * 4) Move the arm using MoveArm()
 * 
 * Any deviation from this sequence will cause errors and unpredictable behaviour (work on this code is still in progress)
 * Also, the SCARA arm operates only in the upper two quadrants meaning the limits for x are: -total arm length <= x <= total arm length
 * The limits for y are 0 <= y <= total arm length. 
 * 
 * Exceeding these limits should give an error
 * 
 * For now, calibration is not included in the script so the user has to manually move the SCARA to the middle position (perpendicular to the base). This point is (0,arm length)
 * 
 * Currently, this sketch is for running a SCARA arm in 2D using 2 NEMA17 motors, 12V, 350 mA, 1.8˚/step and DRV8825 driver boards. The gearing on our arm results in a 90/20 conversion.
 * To adjust this sketch for your needs, you can adjust the SCARA dimensions (length), the degrees/step (degree of joint rotation/step of the motor).
 * Of course pin wiring can also be adjusted. Additionally, speed of the arm can be edited using the stepInterval variables.
 * To increase precision, microstepping can be activated using these driver boards, to reduce the step size. See datasheet for details: https://reprapworld.com/datasheets/datasheet%20drv8825.pdf
 * Our steppers are set such that they both use the same angle/step. If you want to adjust this, you can add another variable or let us know and we can adjust the script to support 
 * this.
 * 
 *  For circuit diagrams see the GitHub repository.
 */

#include <math.h>
#include <Wire.h>

//Constants
  const float pi = M_PI;

//Pin for button input
  int analogPinA0 = A0;
  
//Arm constants
  const float lowerArmLength = 125;
  const float upperArmLength = 125;

//Motor constants
  const int stepPinMot1 = 11;
  const int dirPinMot1 = 12;
  const int stepIntervalMot1 =  1;
  const int Mot1M1 = 8;
  const int Mot1M2 = 9;
  const int Mot1M3 = 10;

  const int stepPinMot2 = 6;
  const int dirPinMot2 = 7;
  const int stepIntervalMot2 =  1;
  const int Mot2M1 = 3;
  const int Mot2M2 = 4;
  const int Mot2M3 = 5;
  
  double degPerStep1 = 1.8/(90/20);
  double degPerStep2 = 1.8/(90/20);

//Arm positioning variables
  float previousElbowX;
  float previousElbowY;
  float elbowX;
  float elbowY;
  float elbowXmin = -upperArmLength;
  float elbowXmax = upperArmLength;
  float elbowYmin = 0;
  float elbowYmax = upperArmLength;
  
  float previousHandX;
  float previousHandY;
  float handX;
  float handY;
  float handXmin = -(upperArmLength+lowerArmLength);
  float handXmax = upperArmLength+lowerArmLength;
  float handYmin = 0;
  float handYmax = upperArmLength+lowerArmLength;
  
  float shoulderAngle;
  float elbowAngle;

  float targetX;
  float targetY;
  
  //Position of the flowpath outlet - these values work for a 96-well plate - need to adjust depending on fraction rack
  const float outletX = 0;
  const float outletY = 140; 
 
  bool positionPossible = true;
  char directionButton;
  
  //Limit buttons
  int button1Pin = 36;
  int button2Pin = 37;
  int button3Pin = 23;
  int button4Pin = 32;

  int button1 = 0;
  int button2 = 0;
  int button3 = 0;
  int button4 = 0;

  bool button1PreviouslyPressed = false;
  bool button2PreviouslyPressed = false;
  bool button3PreviouslyPressed = false;
  bool button4PreviouslyPressed = false;
  bool calibrationFinished = false;

  int CWsteps = 0;
  int CCWsteps = 0;
  int totalSteps = 0;
  
  //State variables
  int state = 0;
  int row = 0;
  int column = 0;
  
  //Communication variables
  byte fracAddress = 11;
  int data = 0;

void setup() {
  
  //Set up Arduino pins
  pinMode(stepPinMot1, OUTPUT);
  pinMode(dirPinMot1,OUTPUT);
  pinMode(stepPinMot2, OUTPUT);
  pinMode(dirPinMot2, OUTPUT);
  pinMode(Mot1M1, OUTPUT);
  pinMode(Mot1M2, OUTPUT);
  pinMode(Mot1M3, OUTPUT);
  pinMode(Mot2M1, OUTPUT);
  pinMode(Mot2M2, OUTPUT);
  pinMode(Mot2M3, OUTPUT);  

  pinMode(analogPinA0,INPUT);
  
  //Set the microstep mode on both motors
  SetMicroStep("1/16",Mot1M1,Mot1M2,Mot1M3, 1);
  SetMicroStep("1/16",Mot2M1,Mot2M2,Mot2M3, 2);

  //Set HandX and HandY variables as well as ElbowX and ElbowY
  elbowX = 0;
  elbowY = upperArmLength;
  handX = 0;
  handY = upperArmLength+lowerArmLength;

  targetX = handX;
  targetY = handY;
  
  //Begin I2C communication and set up event handling for incoming comms
  Wire.begin(fracAddress);
  Wire.onReceive(receiveEvent);
  
  Serial.begin(9600);
}

void loop() 
{
  //Calibrate once get signal from control unit
  while(state == 0)
  {
    //If receive a 1 from the control unit, calibrate
    if(data == 1)
    {
      //Run calibration function
      CalibrateArmPosition();
    }
    if(data == 2)
    {
      state = 1;
    }
    delay(200);  
  }
  
  //Pump calibrated - wait for information to start collecting fractions
  while(state == 1)
  { 
    if(data == 4)
    {
      //Move to next fraction
      nextFraction();     
    }

    if(data == 6)
    {
      //End run and move back to start position
      column = 0;
      row = 0;
      MoveTo(0,250);
      state = 0;
      data = 0;
      break;
    }
  }
}

//Receive data from control unit
void receiveEvent(int nrOfBytes)
{
  //Read in data
  data = Wire.read();
}

//Function to move to the next fraction
void nextFraction()
{
    float xOffset = 14.3;
    float yOffset = 11.2;
    float distanceBetweenWells = 9.0;
    float plateWidth = 127.8;
    float plateHeight = 85.5;
  
    targetX = outletX + (plateWidth/2 - xOffset) - float(column)*distanceBetweenWells;
    targetY = outletY - (plateHeight/2 - yOffset) + float(row)*distanceBetweenWells;

  MoveTo(targetX,targetY);

  //After movement, increment column
  column++;
  
  //check if need to increment row
  if(column >11)
  {
    column = 0;
    row++;
  }
  
   //Set data back to 0
  data = 0;
  
  //If finished the plate, set everything back to 0 and go back to starting position
  if(row >7)
  {
    column = 0;
    row = 0;
    MoveTo(0,250);
    data = 6;
    state = 0;
  }
}

//Function that combines all calls to allow easier use of the program
void MoveTo(float X, float Y)
{
  SaveArmPosition();
  SetTarget(X,Y);
  CalculateElbowPosition();
  MoveArm();
}

  //Saves the current position to the previous position variables
  void SaveArmPosition()
  {
    previousElbowX = elbowX;
    previousElbowY = elbowY;
    previousHandX = handX;
    previousHandY = handY;
  }

  //Sets the target variables, also checks if the target point is inside the defined range of the arm
  void SetTarget(float setX, float setY)
  {
    //Sanity check, can the arm reach, if not, stay in position 
    if(setY >= handYmin && setY <= handYmax && setX >= handXmin && setX <= handXmax)
    {
      targetX = setX;
      targetY = setY;
    }
    else
    {
      Serial.println("Target out of range");
      targetX = handX;
      targetY = handY;
    }
  }

//Calculates the elbow position of the arm for a given target point
void CalculateElbowPosition()
{
  float distance;
  float a;
  float b;
  float h;
  float iX;
  float iY;

  float elbowX1;
  float elbowX2;
  float elbowY1;
  float elbowY2;

  //calculates the distance between the circle midpoints
  distance = sqrt(sq(targetX)+sq(targetY));

  //Error catching
  if(distance > lowerArmLength + upperArmLength)
  {
    Serial.println("Error, position impossible");
    positionPossible = false;
  }
  else if(distance < abs(lowerArmLength - upperArmLength))
  {
    Serial.println("Error, position impossible");
    positionPossible = false;
  }
  else if (distance == 0)
  {
    Serial.println("Error, position impossible");
    positionPossible = false;
  }
  else
  {
    //can move here
    positionPossible = true;
    
    //calculate a and b (distances from the midpoints to the line that goes through both intercept points
    a = (sq(lowerArmLength) - sq(upperArmLength) + sq(distance))/(2*distance);
    b = (sq(upperArmLength) - sq(lowerArmLength) + sq(distance))/(2*distance);

    //calculate h (perpendicular distance from the line between the two midpoints to the intercept points)
    h = sqrt(sq(upperArmLength) - sq(a));

    //calculate the position of point I (point where the line through both intercepts intercepts line through both midpoints
    iY = (a*targetY)/distance;
    iX = (a*targetX)/distance;

    //calculate the position of the elbow
    elbowX1 = iX + ((targetY * h)/distance);
    elbowY1 = iY - ((targetX * h)/distance);
    elbowX2 = iX - ((targetY * h)/distance);
    elbowY2 = iY + ((targetX * h)/distance);

    //Calculate which elbow point causes the least movement of the lower arm within the max range and set the target elbow point accordingly
    if((sqrt(sq(abs(previousElbowX - elbowX1))+sq(abs(previousElbowY - elbowY1))) <= sqrt(sq(abs(previousElbowX - elbowX2))+sq(abs(previousElbowY - elbowY2)))) && 
    elbowXmin <= elbowX1 <= elbowXmax && elbowYmin <= elbowY1 <= elbowYmax)
    {
      elbowX = elbowX1;
      elbowY = elbowY1;
    }
    else
    {
      elbowX = elbowX2;
      elbowY = elbowY2;
    }
  }
}

//Calculates the angle to move the lower arm to, moves lower arm and calculates the new x,y position of the hand then moves upper arm
void MoveArm()
{
  //Calculate shoulder angle using the angle between two vectors, pointing to the previous elbow position and the current elbow position 
  shoulderAngle = atan2(elbowY,elbowX) - atan2(previousElbowY,previousElbowX);
  
  //Convert angle from radians to degrees
  shoulderAngle = shoulderAngle * (180/M_PI);

  //Calculate number of steps - if try to step behind the arm, reverse direction
  if(shoulderAngle >= 180)
  {
    shoulderAngle = shoulderAngle - 360;
  }
  else if (shoulderAngle <= -180)
  {
    shoulderAngle = shoulderAngle + 360;
  }
  int steps = abs(shoulderAngle/degPerStep2);

  //If angle >= 0 move counterclockwise (true) else move clockwise
  if(shoulderAngle >= 0)
  {
    TurnStepper(2,true,steps, stepIntervalMot1);
  }
  else if(shoulderAngle < 0)
  {
    TurnStepper(2,false,steps, stepIntervalMot1);
  }
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

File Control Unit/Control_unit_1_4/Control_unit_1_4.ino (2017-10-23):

 /*
         Biomaker Challenge 2017 - Control unit code
Version 0.8 - added method run capabilities         
Version 0.7 - try adding control of the fraction collector
The pressure sensor library is by Luke Miller and can be found at http://github.com/millerlp
*/

//Include Wire library for I2C communication
#include <Wire.h>

//Include library for pressure sensor
#include <MS5803_14.h>

//Include Grove RGB LCD library
#include "rgb_lcd.h"

//Addresses for I2C devices
byte pump1Address = 9;
byte pump2Address = 10;
byte fracAddress = 11;

//Key inputs for analog buttons
#define UP       0
#define DOWN     1
#define LEFT     2
#define RIGHT    3
#define SELECT   4
#define NOKEY    5
int buttonPin = A3;
int button;

//Start an instance of the rgb_lcd class called lcd
rgb_lcd lcd;

//Variables for cursor position
int cursorX = 0;
int cursorY = 0;

//Variables to monitor menu progression
int state = 0;
int cont = 0;

//Variables for sensor values
int UV;
int UVPin = A2;
float pressureV;

//Setup an object of the pressure sensor class
MS_5803 pressureSensor = MS_5803(512);

//Other variables
int pumpNr = 1;
int flowRate = 0;

void setup()
{
  //Start serial communication
  Serial.begin(9600);
  
  //Start I2C communication
  Wire.begin();
  
  //Setup the LCD - 16 characters per line, 2 lines - background white
  lcd.begin(16,2);
  lcd.setRGB(255,255,255);
  lcd.noBlink();
  lcd.clear();

  //Initialize the MS5803 pressure sensor
  pressureSensor.initializeMS_5803(false);

  //Initialize data pins
  pinMode(UVPin,INPUT);  
}

void loop()
{
 //Title screen
  while (state == 0)
  {
    //Show the title screen
    lcd.setCursor(2,0);
    lcd.print("Open-source");
    lcd.setCursor(4,1);
    lcd.print("FPLC 1.0");
    delay(2000);
    lcd.clear();
    lcd.setCursor(4,0);
    lcd.print("Biomaker");
    lcd.setCursor(1,1);
    lcd.print("Challenge 2017");
    delay(2000);
    lcd.clear();
    state = 1;
  }
  
  //Check connection to I2C devices 
  while(state ==1)
  {
    lcd.setCursor(1,0);
    lcd.print("Connecting....");
    delay(1000);
    
    //Check if pump 1 is connected and display results on LCD
    if(checkI2Cdevice(pump1Address))
    {
      lcd.clear();
      lcd.print("Pump 1 connected");
      delay(1000);
    }
    else
    {
      lcd.clear();
      lcd.setCursor(1,0);
      lcd.print("Cannot connect");
      lcd.setCursor(5,1);
      lcd.print("Pump 1");
      delay(1000);    
    }
    
    //Check if pump 2 is connected and display results on LCD
    if(checkI2Cdevice(pump2Address))
    {
      lcd.clear();
      lcd.print("Pump 2 connected");
      delay(1000);
    }
    else
    {
      lcd.clear();
      lcd.setCursor(1,0);
      lcd.print("Cannot connect");
      lcd.setCursor(5,1);
      lcd.print("Pump 2");
      delay(1000);    
    }
  
    //Check if fraction collector is connected and display results on LCD
    if(checkI2Cdevice(fracAddress))
    {
      lcd.clear();
      lcd.print(" Frac connected ");
      delay(1000);
    }
    else
    {
      lcd.clear();
      lcd.setCursor(1,0);
      lcd.print("Cannot connect");
      lcd.setCursor(6,1);
      lcd.print("Frac");
      delay(1000);    
    }
  
  //Display a menu that allows user to either continue or try to reconnect devices
    lcd.clear();
    lcd.setCursor(4,0);
    lcd.print("Continue");
    lcd.setCursor(4,1);
    lcd.print("Reconnect");
    lcd.setCursor(0,0);
    lcd.blink();
    cursorX = 0;
    cursorY = 0;
    
    //Process input from buttons to allow menu selection
    while(true)
    {
      //Read the input buttons and move cursor according to the choice made (up or down only)
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

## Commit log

2017-10-06 Sketch to control UV sensor
2017-10-07 Added calibration for the shoulder joint
2017-10-07 motor driver datasheet
2017-10-08 Disable calibrate - add microstepping
    Microstepping required for accuracy, Working on getting the calibrate function to work again.
2017-10-08 Add initial syringe pump control sketch
2017-10-15 Syringe pump sketch for control over I2C
2017-10-15 updated control unit code
    Allows manual control of pumps running the syringe pump sketch.
2017-10-15 communicates with frac to calibrate
2017-10-15 enable calibration on prompting over I2C
2017-10-17 calibration and I2C communication added
2017-10-31 Added 3D files for the SCARA fraction collector
    [SCARA_NEMAhousing.stl, SCARA_SBSplateholder.stl, SCARA_arduinomega_housing.stl, SCARA_rearcover.stl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]
2017-10-31 Added 3D files for the MCU
    [MCU v3.step, MCU_base.stl, MCU_cover.stl]
2017-10-31 Added 3D files for the syringe pump.
    [pump_12Vclamp.stl, pump_adapterluer.stl, pump_base.stl, pump_baseplate.stl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]
2017-10-31 Added 3D files for the UV flow cell
    [UV flow cell_2tubes_uv components v14.step, flowcell_cover_detector.stl, flowcell_cover_led.stl, flowcell_holder.stl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]
2017-10-31 3d files added
    [mixer_unit.stl, pressure_sensor_housing.stl, swingarm_inner.stl, swingarm_outer.stl]
